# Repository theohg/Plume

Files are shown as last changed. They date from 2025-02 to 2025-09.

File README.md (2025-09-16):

<p align="center" width="100%">
  <picture>
    <source media="(prefers-color-scheme: dark)" srcset="./Logos/Plume_logo_light.png">
    <source media="(prefers-color-scheme: light)" srcset="./Logos/Plume_logo_dark.png">
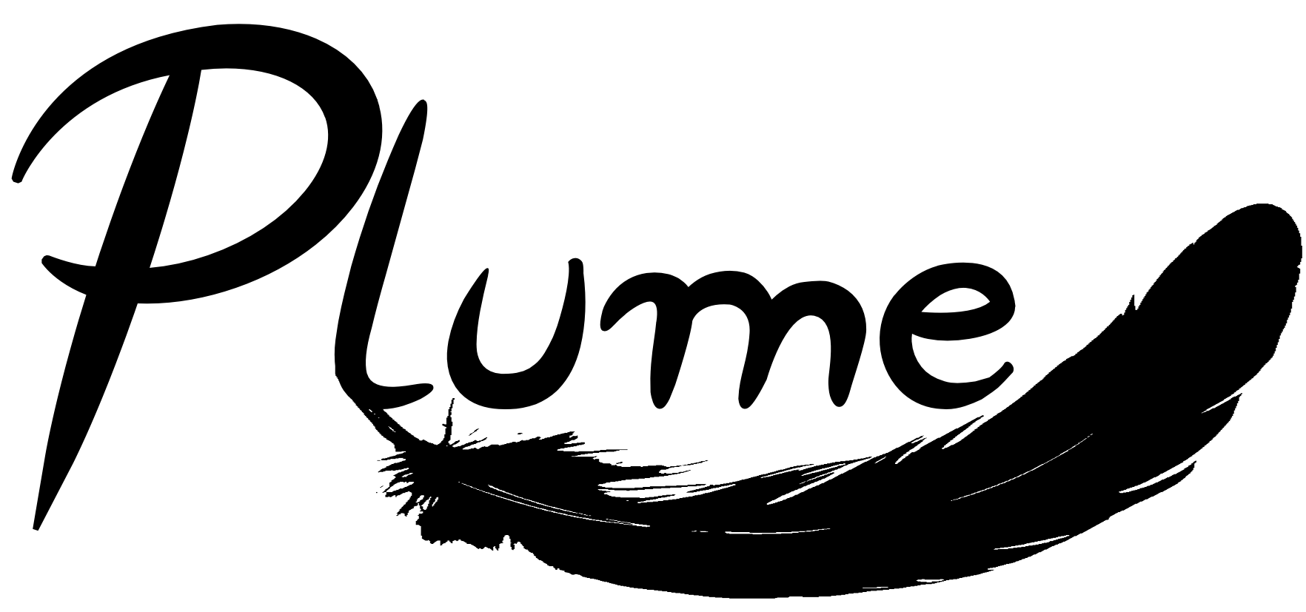
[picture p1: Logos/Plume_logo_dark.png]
Plume logo
    
  </picture>
</p>

Plume was designed by Théo Heng for the Integrated Actuators Laboratory [(LAI)](https://www.epfl.ch/labs/lai/) in the context of a master semester project. The goal is to develop a microcontroller-based system to independently control a motor array in a reconfigurable insole designed for patients with diabetes, redistributing plantar pressure without the use of position sensors. 

This board is capable to drive and control in position up to 18 Brushed DC motors total and up to 9 simultaneously, without position sensors. This is achieved thanks to the ripple counting technique, integrated in the DRV8214 drivers. 

Plume also integrates multiple other features: 
- Automotive Grade Wireless Charging Qi (WPC v2.0) 
- USB-C charging
- Power Path between USB and Induction
- BLE 5.4
- Adressable RGB LED
- Power LED, Charge LED, Fault LEDs
- Exposed UART and I2C interface
- Tag-Connect 2030 for SWD + SWO
- Battery Protection and Voltage Supervisor
- 6-axis, High Performance, low power IMU
- Motion-Controlled Deep-Sleep mode
- I2C Multiplexer
- Accurate and Low-Power Battery Voltage Sensing

***

<p align="center" width="100%">
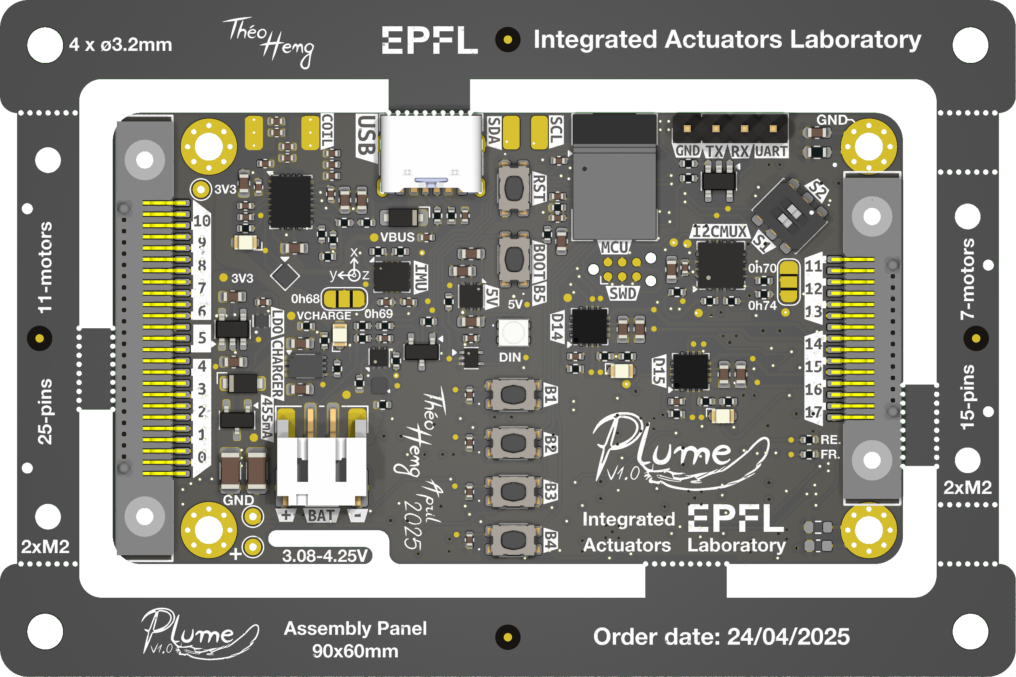
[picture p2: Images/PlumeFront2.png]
    
</p>

<p align="center" width="100%">
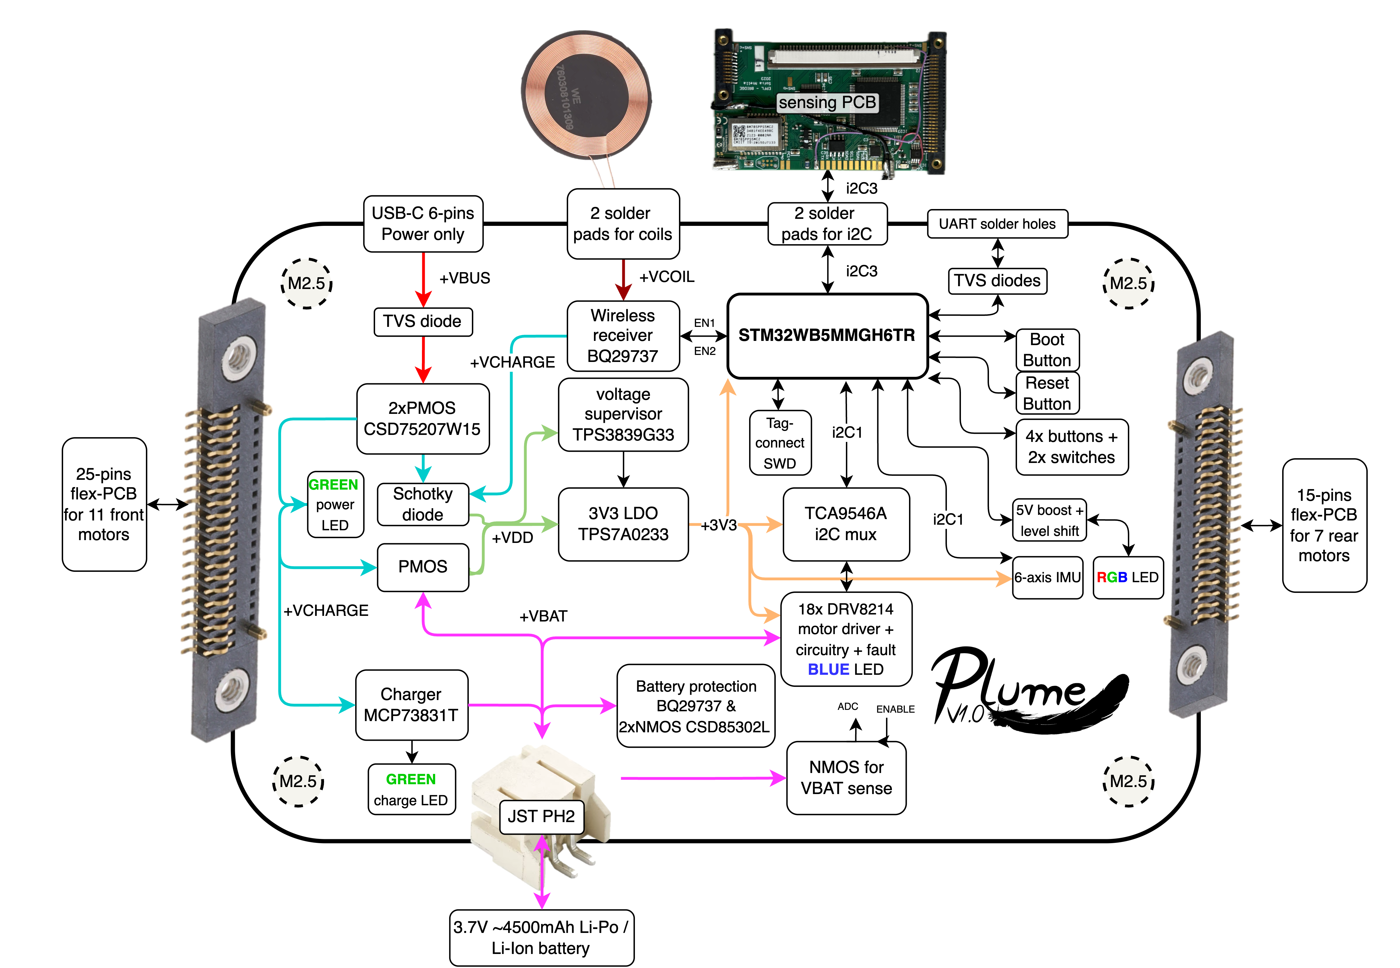
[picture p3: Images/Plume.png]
    
</p>

***

## SPECIFICATIONS

| Parameter | Plume V1.0 | 
| --- | --- |
| Working Battery Voltage Input | 3.08-4.25 V |
| Typ. Charge Current (USB, wireless)| 455 mA |
| Max. Allowed Charge Current | 2.27 A |
| Max. Continuous Discharge Current | 4.54 A |
| Theoretical Deep Sleep Power Consumption| 15 µA |
| Mass | 23.5g with the frame |
| Communication | UART / Trace Asynchronous (SWD) / I2C |
| MCU | STM32 WB5MMGH6TR |
| Dimensions | 70x40x9mm |
| Cost per PCB    | 39 CHF board + 75 CHF components + 125 CHF assembly ≈ 240 CHF / PCB    |
| Designer   | Théo Heng        |
| Supervisors   | Maël Dagon, Paolo Germano      |
| Development Period       | Feb. - May. 2025 |
| Project    | Smart Footwear for Diabetic Foot Care    |

***

## DIRECTORY STRUCTURE

```
Plume
├── Computations        # Computation sheets and simulations performed
├── Datasheets          # Datasheet of components
├── Images              # Pictures and screenshots used in schematics
├── lib
    |── 3d_models       # Component 3D models
    |── lib_fp          # Footprint libraries
    └── lib_sym         # Symbol libraries
├── Logos               # EPFL and Plume logos
├── Manufacturing
    |── Assembly        # BOM, assembly document
        |── bom.csv     # CSV BOM
        |── bom.html    # HTML BOM
        └── ibom        # HTML interactive BOM
    └── Fabrication     # zipped fabrication documents, and other generated documents by JLCToolkit Pluggin
├── Schematic           # PDF of schematic
├── Software            # Firmware of the Board
    |── PLUME_ESP32     # PlatformIO project for the ESP32-based prototype
    └── PLUME_STM32     # STM32CubeIDE project for the Plume PCB
├── STEP_BLENDER_STL    # Step, .pcb3d and stl files of the PCB and its casing
└── Templates           # Title block templates

```

***

## FIRMWARE

<p align="center" width="100%">
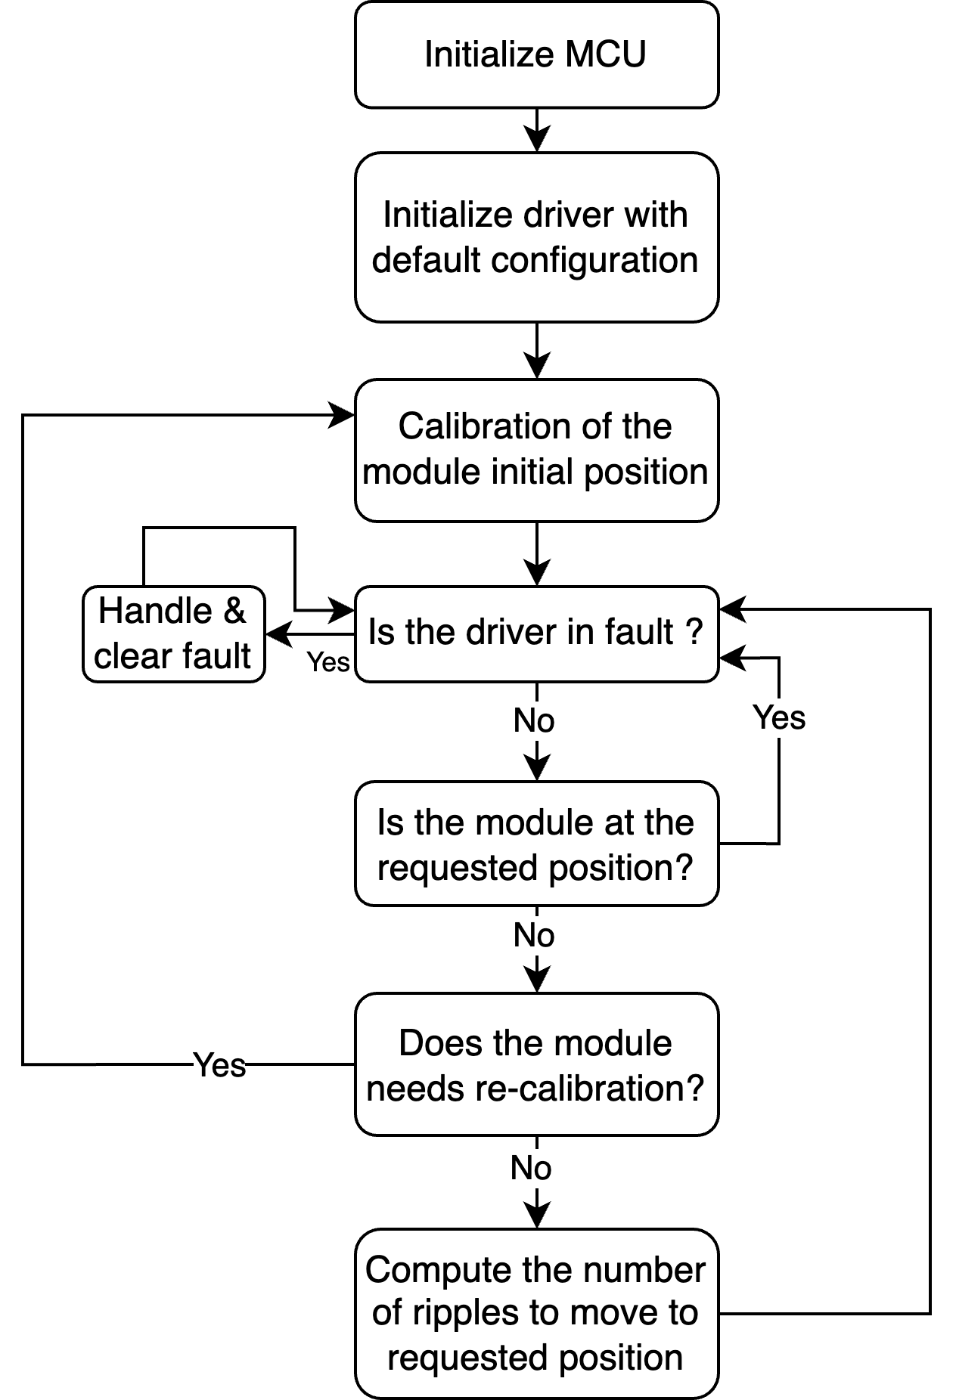
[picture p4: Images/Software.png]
    
</p>

***

## CREDITS

Schematic template & project structure is hugely inspired by the work of Vincent Nguyen on its [Λ M U L E T](https://github.com/EPFLXplore/XRE_LeggedRobot_HW/tree/master/amulet_controller) controler.

***

## PHOTOS

<p align="center" width="100%">
    
</p>

<p align="center" width="100%">
    
</p>

<p align="center" width="100%">
    
</p>

<p align="center" width="100%">
    
</p>

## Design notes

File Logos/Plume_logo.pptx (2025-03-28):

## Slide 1

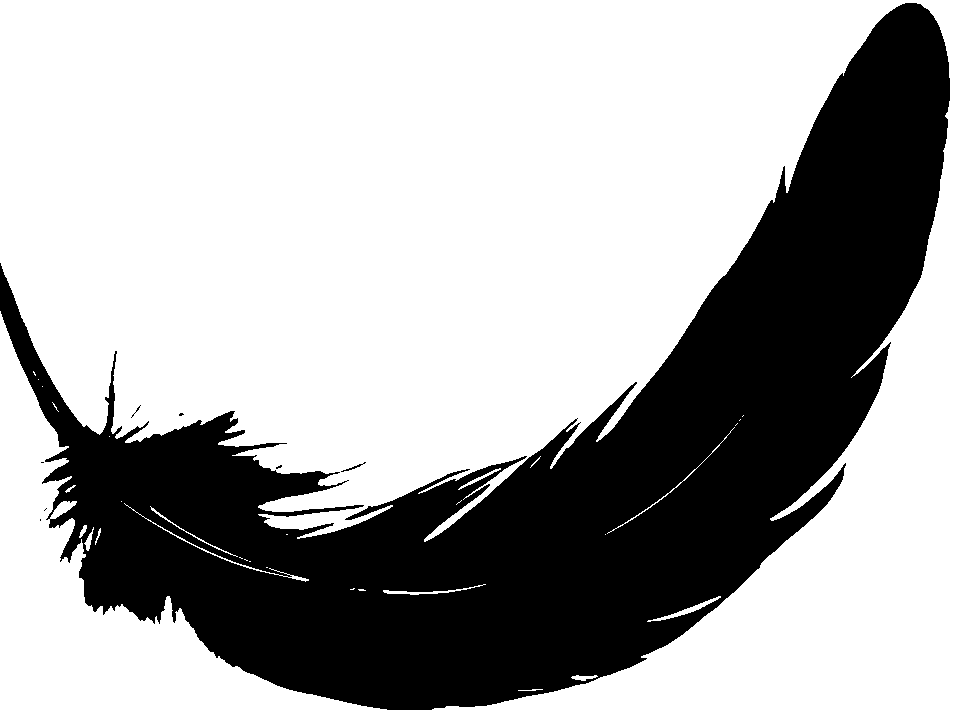
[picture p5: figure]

Plume

V1.0

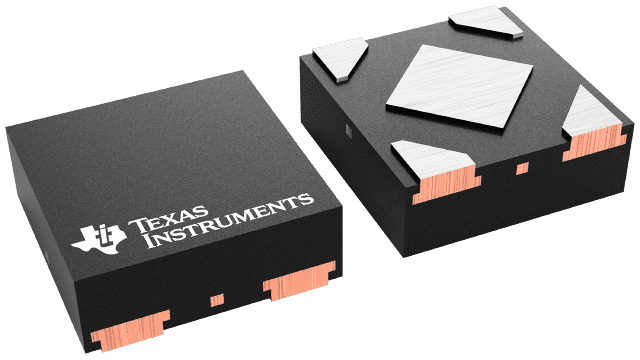
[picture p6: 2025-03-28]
Images/Packages/X2SON_package.png

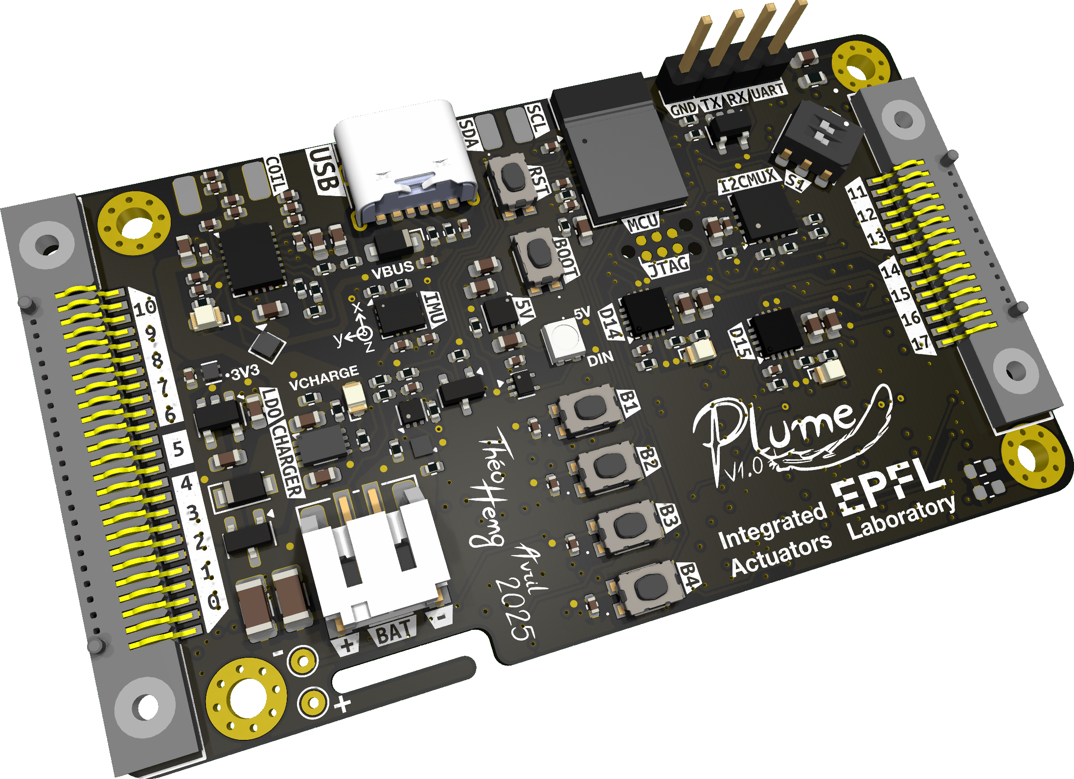
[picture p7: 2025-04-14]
Images/PlumeFront1.png

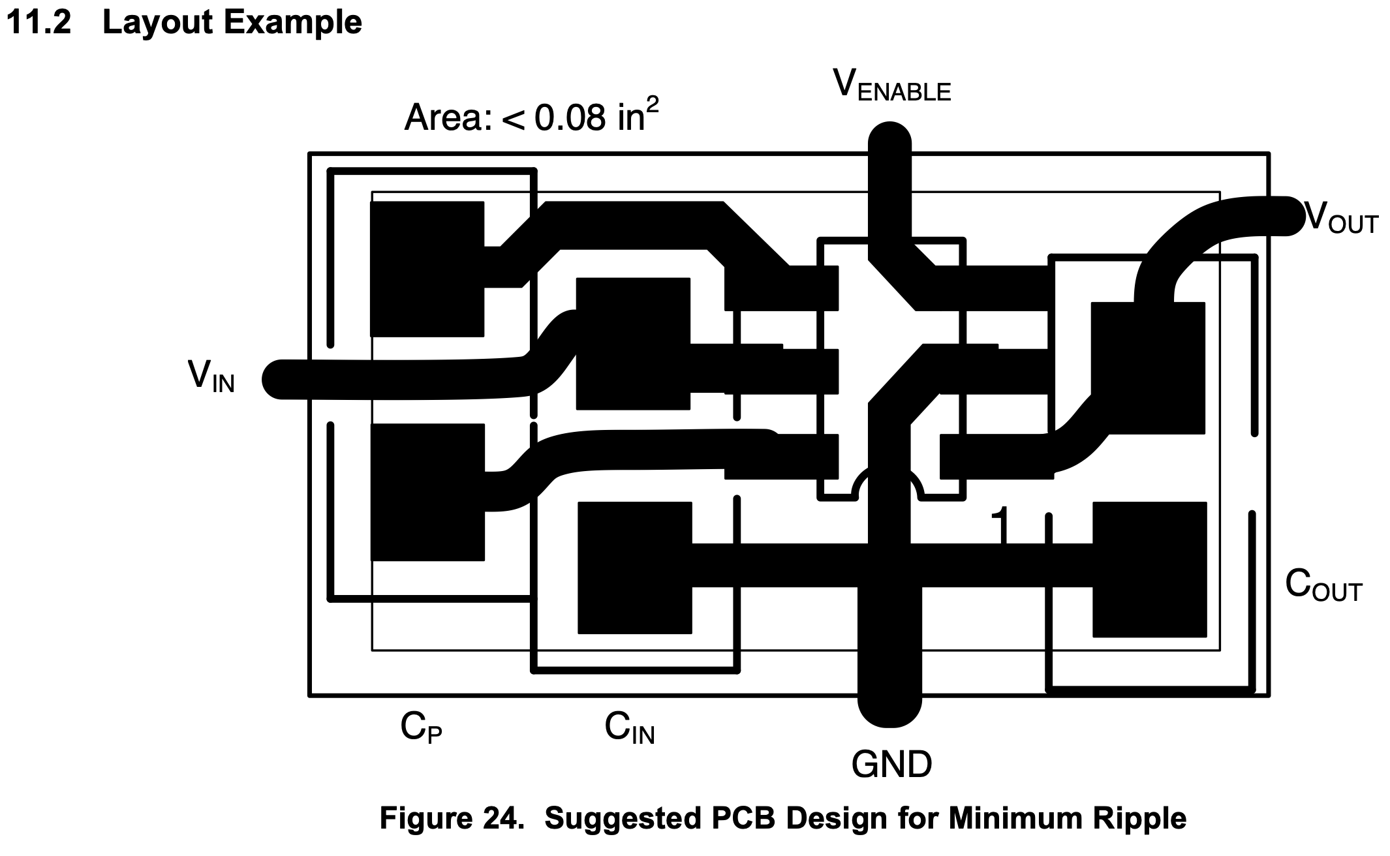
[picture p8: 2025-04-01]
Images/Layouts/Layout_REG71050.png

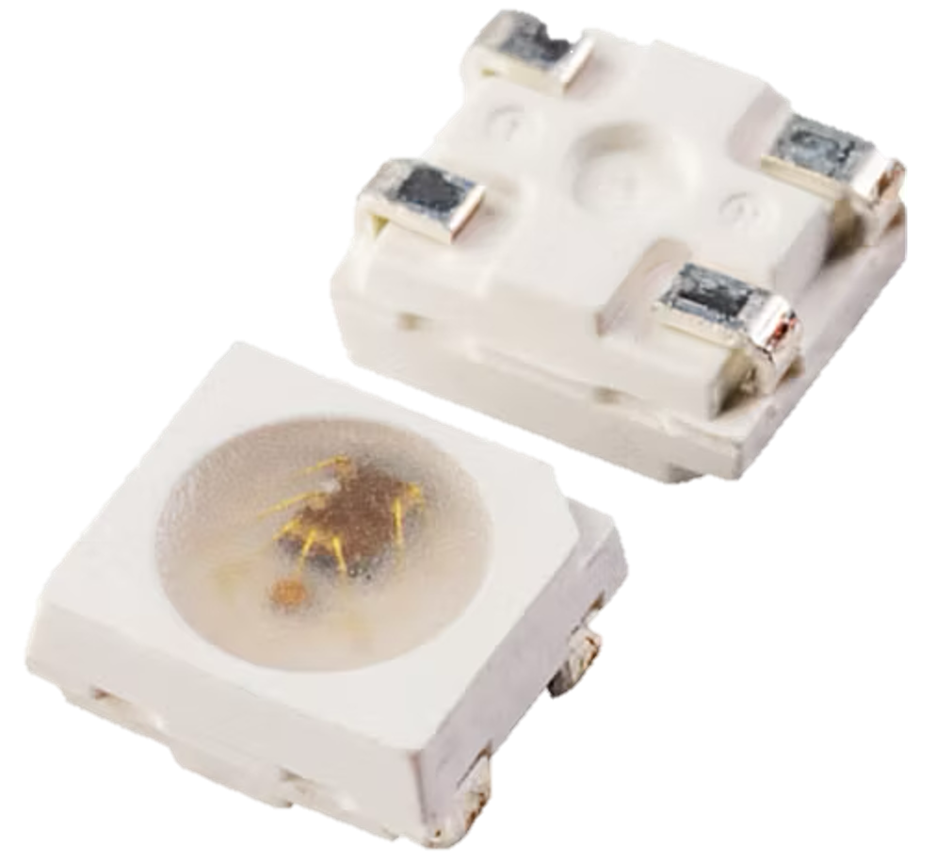
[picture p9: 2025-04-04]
Images/Packages/2427_RGB_LED.png

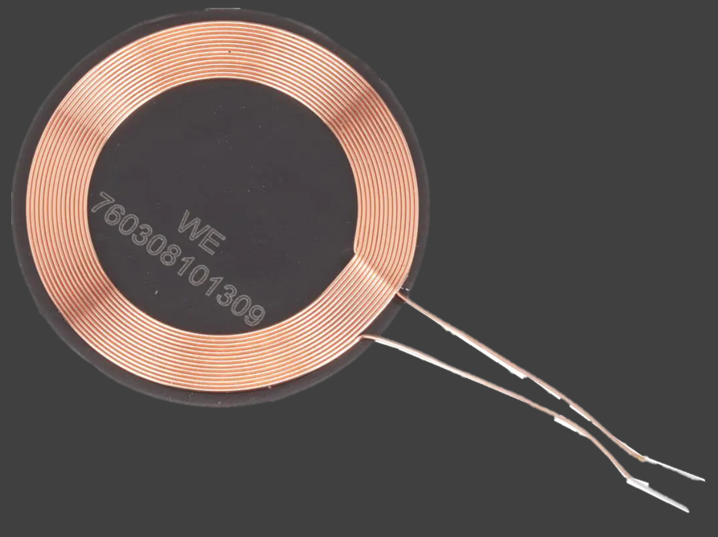
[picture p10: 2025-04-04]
Images/Packages/Coil.png

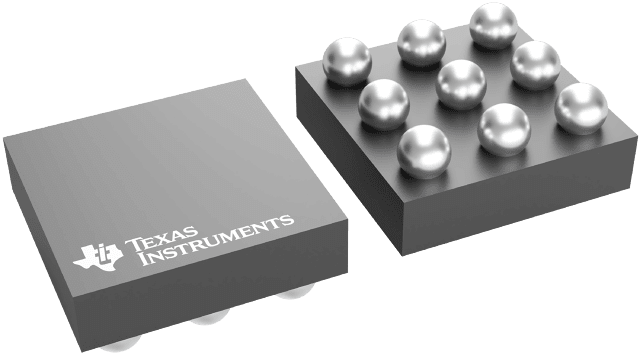
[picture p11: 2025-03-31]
Images/Packages/DSBGA-9_package.png

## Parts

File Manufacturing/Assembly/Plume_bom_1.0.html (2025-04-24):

Source File | Plume.kicad_sch
BoM Date | 2025-04-24T23:43:28+0200
Schematic Version | 1.0
Schematic Date | 2025-04-21
PCB Variant | default
KiCad Version | Eeschema 9.0.0
Component Groups | 53
Component Count (per PCB) | 257
Fitted Components (per PCB) | 251
Number of PCBs | 1
Total Component Count (for 1 PCBs) | 251
 | Description | Part | References | Value | Footprint | Quantity Per PCB | Datasheet | Manufacturer Part Number | Manufacturer | Supplier | Supplier Part Number
1 | Unpolarized capacitor | C_Small | C401 C402 C407 C408 C409 C410 C504 C505 C601 C604 C605 C616 C701 C801 C903 C1001 C1002 C1203 C1303 C1403 C1503 C1603 C1703 C1803 C1903 C2003 C2103 C2203 C2303 C2403 C2503 C2603 C2703 C2803 C2903 | 100n X7R 16V | C_0402_1005Metric | 35 | https://www.mouser.ch/ProductDetail/Samsung-Electro-Mechanics/CL05B104KO5VPNC?qs=SRYZG9HaIQ0dGqjRr5dbew%3D%3D | CL05B104KO5VPNC | Samsung Electro-Mechanics | Mouser Electronics | 187-CL05B104KO5VPNC (https://www.mouser.com/ProductDetail/187-CL05B104KO5VPNC)
2 | Unpolarized capacitor | C_Small | C1202 C1302 C1402 C1502 C1602 C1702 C1802 C1902 C2002 C2102 C2202 C2302 C2402 C2502 C2602 C2702 C2802 C2902 | 100n X7R 50V | C_0603_1608Metric | 18 | https://www.mouser.ch/ProductDetail/KEMET/C0603C104J5RACAUTO?qs=XYJIsZbdjSO3ULwa1DwJaA%3D%3D | C0603C104J5RACAUTO | KEMET | Mouser Electronics | 80-C0603C104J5RAUTO (https://www.mouser.com/ProductDetail/80-C0603C104J5RAUTO)
3 | Unpolarized capacitor | C_Small | C606 C609 C615 | 10n C0G 25V | C_0402_1005Metric | 3 | https://www.mouser.ch/ProductDetail/Murata-Electronics/GRM1555C1E103JE01J?qs=d0WKAl%252BL4Kaf0f%252BHGWOwHQ%3D%3D | GRM1555C1E103JE01J | Murata Electronics | Mouser Electronics | 81-GRM1555C1E103JE1J (https://www.mouser.com/ProductDetail/81-GRM1555C1E103JE1J)
4 | Unpolarized capacitor | C_Small | C602 C617 C618 C702 C703 C1201 C1301 C1401 C1501 C1601 C1701 C1801 C1901 C2001 C2101 C2201 C2301 C2401 C2501 C2601 C2701 C2801 C2901 | 10u X5R 16V | C_0603_1608Metric | 23 | https://www.mouser.ch/ProductDetail/Murata-Electronics/GRM188R61C106MAALD?qs=hNud%2FORuBR3LEOKZ4RJp9w%3D%3D | GRM188R61C106MAALD | Murata Electronics | Mouser Electronics | 81-GRM188R61C106MALD (https://www.mouser.com/ProductDetail/81-GRM188R61C106MALD)
5 | Unpolarized capacitor | C_Small | C610 | 150n X7R 25V | C_0402_1005Metric | 1 | https://www.mouser.ch/ProductDetail/TDK/CGA2B3X7R1E154K050BB?qs=xLDY6iXSiQa5a3ygyaobCg%3D%3D | CGA2B3X7R1E154K050BB | TDK | Mouser Electronics | 810-CGA2B3X7R1E154KB (https://www.mouser.com/ProductDetail/810-CGA2B3X7R1E154KB)
6 | Unpolarized capacitor | C_Small | C3002 | 1n X7R 1kV | C_0603_1608Metric | 1 | https://www.mouser.ch/ProductDetail/KEMET/C0603C102KDRACTU?qs=B0TNOcbsrWfl%252B1TgqaaQlQ%3D%3D | C0603C102KDRACTU | KEMET | Mouser Electronics | 80-C0603C102KDRACTU (https://www.mouser.com/ProductDetail/80-C0603C102KDRACTU)
7 | Unpolarized capacitor | C_Small | C603 C802 | 1u X7R 16V | C_0603_1608Metric | 2 | https://www.mouser.ch/ProductDetail/TDK/CGA3E1X7R1C105K080AC?qs=XHchNesRtUbBVNsGg9%252BP9g%3D%3D | CGA3E1X7R1C105K080AC | TDK | Mouser Electronics | 810-CGA3E1X7R1C105AC (https://www.mouser.com/ProductDetail/810-CGA3E1X7R1C105AC)
8 | Unpolarized capacitor | C_Small | C901 | 220n X7R 16V | C_0603_1608Metric | 1 | https://www.mouser.ch/ProductDetail/TDK/CGA3E2X7R1C224K080AA?qs=NRhsANhppD%252BSF2Ghb8qyBQ%3D%3D | CGA3E2X7R1C224K080AA | TDK | Mouser Electronics | 810-CGA3E2X7R1C224K (https://www.mouser.com/ProductDetail/810-CGA3E2X7R1C224K)
9 | Unpolarized capacitor | C_Small | C608 C614 | 22n X7R 25V | C_0402_1005Metric | 2 | https://www.mouser.ch/ProductDetail/Murata-Electronics/GCM155R71E223KA55D?qs=QDXoN8f0aYJ3xbAG%252B51q9g%3D%3D | GCM155R71E223KA55D | Murata Electronics | Mouser Electronics | 81-GCM155R71E223KA5D (https://www.mouser.com/ProductDetail/81-GCM155R71E223KA5D)
10 | Unpolarized capacitor | C_Small | C611 | 2n2 X7R 25V | C_0402_1005Metric | 1 | https://www.mouser.ch/ProductDetail/TAIYO-YUDEN/TMF105B7222KVHF?qs=%252B6g0mu59x7L2OaVQBnCjqw%3D%3D | TMF105B7222KVHF | TAIYO YUDEN | Mouser Electronics | 963-TMF105B7222KVHF (https://www.mouser.com/ProductDetail/963-TMF105B7222KVHF)
11 | Unpolarized capacitor | C_Small | C902 C904 | 2u2 X7R 16V | C_0603_1608Metric | 2 | https://www.mouser.ch/ProductDetail/Murata-Electronics/GRM188Z71C225KE43D?qs=Ey7%2FXF42M3cR7ECLHyzpoA%3D%3D | GRM188Z71C225KE43D | Murata Electronics | Mouser Electronics | 81-GRM188Z71C225KE3D (https://www.mouser.com/ProductDetail/81-GRM188Z71C225KE3D)
12 | Unpolarized capacitor | C_Small | C612 | 390pF X7R 25V | C_0402_1005Metric | 1 | https://www.mouser.ch/ProductDetail/Vishay-Vitramon/VJ0402Y391JXXCW1BC?qs=f5fGhOx873TBeKjaAqsdYg%3D%3D | VJ0402Y391JXXCW1BC | Vishay / Vitramon | Mouser Electronics | 77-VJ0402Y391JXXCBC (https://www.mouser.com/ProductDetail/77-VJ0402Y391JXXCBC)
13 | Unpolarized capacitor | C_Small | C607 C613 | 470n X5R 25V | C_0402_1005Metric | 2 | https://www.mouser.ch/ProductDetail/Murata-Electronics/GRT155R61E474KE01D?qs=drgMNd%252BkGPMC62u63CQDfw%3D%3D | GRT155R61E474KE01D | Murata Electronics | Mouser Electronics | 81-GRT155R61E474KE1D (https://www.mouser.com/ProductDetail/81-GRT155R61E474KE1D)
14 | Unpolarized capacitor | C_Small | C501 C502 | 47u X5R 16V | C_1206_3216Metric | 2 | https://www.mouser.ch/ProductDetail/TAIYO-YUDEN/MSASE31LBB5476MTNA01?qs=tlsG%2FOw5FFhhPmEmFzorng%3D%3D | MSASE31LBB5476MTNA01 | TAIYO YUDEN | Mouser Electronics | 963-MSASE31LBB5476MT (https://www.mouser.com/ProductDetail/963-MSASE31LBB5476MT)
15 | Unpolarized capacitor | C_Small | C403 C503 C506 | 4u7 X7R 16V | C_0603_1608Metric | 3 | https://www.mouser.ch/ProductDetail/Murata-Electronics/GRM188Z71C475KE21D?qs=d0WKAl%252BL4KajNOvalhHKtQ%3D%3D | GRM188Z71C475KE21D | Murata Electronics | Mouser Electronics | 81-GRM188Z71C475KE1D (https://www.mouser.com/ProductDetail/81-GRM188Z71C475KE1D)
16 | ESD Protection Diodes / TVS Diodes Quad 4.5-pF 3.6-V +/-30-kV ESD protect | ESDS314 | D401 | ESDS314 | SOT-23-5-TEXAS | 1 | https://www.ti.com/lit/ds/symlink/esds314.pdf?ts=1743702062530 | ESDS314DBVR | Texas Instruments | Mouser Electronics | 595-ESDS314DBVR (https://www.mouser.com/ProductDetail/595-ESDS314DBVR)
17 | 2427 RGB LED 4-Pin with Integrated IC | IN-PI22TAT5R5G5B | D901 | IN-PI22TAT5R5G5B | INPI22TAT5R5G5B | 1 | https://www.inolux-corp.com/datasheet/SMDLED/Addressable%20LED/IN-PI22TAT5R5G5B_v1.2.pdf | IN-PI22TAT5R5G5B | Inolux | Mouser Electronics | 743-IN-PI22TAT5R5G5B (https://www.mouser.com/ProductDetail/743-IN-PI22TAT5R5G5B)
18 | Schottky diode | D_Schottky | D701 | Schottky 1N5819W | Nexperia_CFP3_SOD-123W | 1 | https://assets.nexperia.com/documents/data-sheet/PMEG60T20ELR.pdf | PMEG60T20ELRX | Nexperia | Mouser Electronics | 771-PMEG60T20ELRX (https://www.mouser.com/ProductDetail/771-PMEG60T20ELRX)
19 | Zener diode | D_Zener | D601 | TVS SMF5.0A | D_SOD-123FL | 1 | https://www.littelfuse.com/assetdocs/tvs-diodes-smf-datasheet?assetguid=7EB8A5B6-BDD0-4561-8F19-0C3CC6F9B2AF | SMF5.0A | Littelfuse | Mouser Electronics | 576-SMF5.0A (https://www.mouser.com/ProductDetail/576-SMF5.0A)
20 | 2-A Brushed DC Motor Driver with Ripple Counting, Stall Detection, and Speed Regulation | DRV8214RTER | IC1201 IC1301 IC1401 IC1501 IC1601 IC1701 IC1801 IC1901 IC2001 IC2101 IC2201 IC2301 IC2401 IC2501 IC2601 IC2701 IC2801 IC2901 | DRV8214RTER | WQFN-16-1EP_3x3mm_P0.5mm_EP1.68x1.68mm_ThermalVias | 18 | https://www.ti.com/lit/ds/symlink/drv8214.pdf?ts=1743082368801 | DRV8214RTER | Texas Instruments | Mouser Electronics | 595-DRV8214RTER (https://www.mouser.com/ProductDetail/595-DRV8214RTER)
21 | 60-mA, 5.0-V, Buck/Boost Charge Pump in ThinSOT-23 | REG71050DRVT | IC902 | REG71050DRVR | WSON-6-1EP_2x2mm_P0.65mm_EP1x1.6mm | 1 | https://www.ti.com/lit/ds/symlink/reg71050.pdf?ts=1743455923124 | REG71050DRVR | Texas Instruments | Mouser Electronics | 595-REG71050DRVR (https://www.mouser.com/ProductDetail/595-REG71050DRVR)
22 | Single Bus Buffer Gate With 3-State Output | SN74AHCT1G125DRLR | IC901 | SN74AHCT1G125DRLR | SOT-553 | 1 | https://www.ti.com/lit/ds/symlink/sn74ahct1g125.pdf?ts=1743406415648 | SN74AHCT1G125DRLR | Texas Instruments | Mouser Electronics | 595-SN74AHCT1G125DRL (https://www.mouser.com/ProductDetail/595-SN74AHCT1G125DRL)
23 | CONN HEADER SMD R/A 2POS 2MM | CONN_S2B-PH-SM4-TB_JST | J502 | S2B-PH-SM4-TB | CONN_S2B-PH-SM4-TB_JST | 1 | https://www.jst-mfg.com/product/pdf/eng/ePH.pdf | S2B-PH-SM4-TB(LF)(SN) | JST Commercial | Mouser Electronics | 306-S2BPHSM4TBLFSN (https://www.mouser.com/ProductDetail/306-S2BPHSM4TBLFSN)
24 | USB Power-Only 6P Type-C Receptacle connector | USB_C_Receptacle_PowerOnly_6P | J602 | USB_C_Receptacle_PowerOnly_6P | USB4125-GF-A | 1 | https://www.mouser.ch/datasheet/2/837/GCT_USB4125_Product_Drawing-3538561.pdf | USB4125-GF-A | GCT | Mouser Electronics | 640-USB4125-GF-A (https://www.mouser.com/ProductDetail/640-USB4125-GF-A)
25 | Single Colour LEDs 0603 Dome Lens LED Blue- 465nm | LED | LED1201 LED1301 LED1401 LED1501 LED1601 LED1701 LED1801 LED1901 LED2001 LED2101 LED2201 LED2301 LED2401 LED2501 LED2601 LED2701 LED2801 LED2901 | BLUE | LED_0603_KingBright | 18 | https://www.mouser.ch/datasheet/2/216/APTD1608LQBC_D-1102154.pdf | APTD1608LQBC/D | Kingbright | Mouser Electronics | 604-APTD1608LQBCD (https://www.mouser.com/ProductDetail/604-APTD1608LQBCD)
26 | Light emitting diode | LED | LED501 LED601 | GREEN | LED_0603_KingBright | 2 | https://www.mouser.ch/datasheet/2/216/APT1608CGCK-24002.pdf | APT1608CGCK | Kingbright | Mouser Electronics | 604-APT1608CGCK (https://www.mouser.com/ProductDetail/604-APT1608CGCK)
27 | MOSFET Dual P-CH NexFET Pwr MOSFET | CSD75207W15 | Q601 | CSD75207W15 | Texas_DSBGA-9_1.62x1.58mm_Layout3x3_P0.5mm | 1 | https://www.ti.com/lit/ds/symlink/csd75207w15.pdf?ts=1743083254353 | CSD75207W15 | Texas Instruments | Mouser Electronics | 595-CSD75207W15 (https://www.mouser.com/ProductDetail/595-CSD75207W15)
28 | 20V, N ch NexFET MOSFET, dual common drain LGA 1.35x1.35, 24mOhm | CSD85302L | Q502 | CSD85302L | CSD85302L | 1 | http://www.ti.com/lit/ds/symlink/csd85302l.pdf | CSD85302L | Texas Instruments | Mouser Electronics | 595-CSD85302L (https://www.mouser.com/ProductDetail/595-CSD85302L)
29 | MOSFETs MOSFT 5.0A 29mOhm 30V 2.5V drv capable | Q_NMOS_Depletion_GSD | Q501 | NMOS IRLML6344TRPBF SOT-23 | SOT-23 | 1 | https://www.mouser.ch/datasheet/2/196/Infineon_IRLML6344_DataSheet_v01_01_EN-3363406.pdf | IRLML6344TRPBF | Infineon Technologies | Mouser Electronics | 942-IRLML6344TRPBF (https://www.mouser.com/ProductDetail/942-IRLML6344TRPBF)
30 | P-MOSFET transistor, gate/source/drain | Q_PMOS_GSD | Q701 | PMOS SI2365EDS-T1-GE3 | SOT-23-3 | 1 | https://www.vishay.com/docs/63199/si2365eds.pdf | SI2365EDS-T1-GE3 | Vishay Semiconductors | Mouser Electronics | 78-SI2365EDS-T1-GE3 (https://www.mouser.com/ProductDetail/78-SI2365EDS-T1-GE3)
31 | Resistor, small symbol | R_Small | R3002 | 0R 1% | R_0603_1608Metric | 1 | https://www.mouser.ch/ProductDetail/YAGEO/RC0603FR-100RL?qs=gY0y7AQI9SNjcfwXbqIKbg%3D%3D | RC0603FR-100RL | YAGEO | Mouser Electronics | 603-RC0603FR-100RL (https://www.mouser.com/ProductDetail/603-RC0603FR-100RL)
32 | Resistor | R_Small | R404 R406 R509 R701 R801 R901 R1203 R1303 R1403 R1503 R1603 R1703 R1803 R1903 R2003 R2103 R2203 R2303 R2403 R2503 R2603 R2703 R2803 R2903 | 100k 1% | R_0402_1005Metric | 24 | https://www.mouser.ch/ProductDetail/Panasonic/ERJ-2RKF1003X?qs=H7k1u0Mp9JQnXoBKdf15Qg%3D%3D | ERJ-2RKF1003X | Panasonic | Mouser Electronics | 667-ERJ-2RKF1003X (https://www.mouser.com/ProductDetail/667-ERJ-2RKF1003X)
33 | Resistor | R_Small | R402 R503 R605 R606 R608 | 10k 1% | R_0402_1005Metric | 5 | https://www.mouser.ch/ProductDetail/KOA-Speer/RK73H1ETTPB1002F?qs=sGAEpiMZZMvdGkrng054t65cMycmke1dK22GtXiM9hM%3D | RK73H1ETTPB1002F | KOA Speer | Mouser Electronics | 660-RK73H1ETTPB1002F (https://www.mouser.com/ProductDetail/660-RK73H1ETTPB1002F)
34 | Resistor | R_Small | R604 R607 | 196R 1% | R_0402_1005Metric | 2 | https://www.mouser.ch/ProductDetail/Vishay-Dale/CRCW0402196RFKED?qs=9Aka%2FNDvCXC%2FtFusjSrxBQ%3D%3D | CRCW0402196RFKED | Vishay / Dale | Mouser Electronics | 71-CRCW0402196RFKED (https://www.mouser.com/ProductDetail/71-CRCW0402196RFKED)
35 | Resistor | R_Small | R403 R405 | 22R 1% | R_0402_1005Metric | 2 | https://www.mouser.ch/ProductDetail/KOA-Speer/RK73H1ETTP22R0F | RK73H1ETTP22R0F | KOA Speer | Mouser Electronics | 660-RK73H1ETTP22R0F (https://www.mouser.com/ProductDetail/660-RK73H1ETTP22R0F)
36 | Resistor | R_Small | R504 R508 | 2k2 1% | R_0402_1005Metric | 2 | https://www.mouser.ch/ProductDetail/KOA-Speer/RK73H1ETTP2201F?qs=oI046glRuruobG9rEu19Sw%3D%3D | RK73H1ETTP2201F | KOA Speer | Mouser Electronics | 660-RK73H1ETTP2201F (https://www.mouser.com/ProductDetail/660-RK73H1ETTP2201F)
37 | Resistor | R_Small | R401 R501 R505 R601 R1202 R1302 R1402 R1502 R1602 R1702 R1802 R1902 R2002 R2102 R2202 R2302 R2402 R2502 R2602 R2702 R2802 R2902 | 330R 1% | R_0402_1005Metric | 22 | https://www.mouser.ch/ProductDetail/KOA-Speer/RK73H1ETTP3300F?qs=4CJzfoelV6C3hCuuGB%2F5LQ%3D%3D | RK73H1ETTP3300F | KOA Speer | Mouser Electronics | 660-RK73H1ETTP3300F (https://www.mouser.com/ProductDetail/660-RK73H1ETTP3300F)
38 | Resistor | R_Small | R502 R802 R803 R804 R805 R806 R807 R1001 R1002 | 3k 1% | R_0402_1005Metric | 9 | https://www.mouser.ch/ProductDetail/KOA-Speer/RK73H1ETTP3001F?qs=pim%252BJ6MgNfS80Tm8%2FkBkXQ%3D%3D | RK73H1ETTP3001F | KOA Speer | Mouser Electronics | 660-RK73H1ETTP3001F (https://www.mouser.com/ProductDetail/660-RK73H1ETTP3001F)
39 | Resistor | R_Small | R506 R507 | 4M99 1% | R_0402_1005Metric | 2 | https://www.mouser.ch/ProductDetail/KOA-Speer/RK73H1ETTP4994F?qs=v3ImdA%2FOTSQZBfUeBz4Q8A%3D%3D | RK73H1ETTP4994F | KOA Speer | Mouser Electronics | 660-RK73H1ETTP4994F (https://www.mouser.com/ProductDetail/660-RK73H1ETTP4994F)
40 | Resistor | R | R602 R603 | 5k1 1% | R_0402_1005Metric | 2 | https://www.mouser.ch/ProductDetail/KOA-Speer/RK73H1ETTP5101F?qs=0Mn4dg0AsPAhhJD1ZsgV0Q%3D%3D | RK73H1ETTP5101F | KOA Speer | Mouser Electronics | 660-RK73H1ETTP5101F (https://www.mouser.com/ProductDetail/660-RK73H1ETTP5101F)
41 | Resistor | R_Small | R1201 R1301 R1401 R1501 R1601 R1701 R1801 R1901 R2001 R2101 R2201 R2301 R2401 R2501 R2601 R2701 R2801 R2901 | 680R 1% | R_0402_1005Metric | 18 | https://www.mouser.fr/ProductDetail/Vishay-Dale/CRCW0402680RFKEDC?qs=E3Y5ESvWgWPmgUvh1o91RA%3D%3D | CRCW0402680RFKEDC | Vishay / Dale | Mouser Electronics | 71-CRCW0402680RFKEDC (https://www.mouser.com/ProductDetail/71-CRCW0402680RFKEDC)
42 | Slide Switches Dual SPDT, ON-ON, slide, J-hook SMD terminals, 100mA @ 6V DC, T&R packaging, non-washable without seal tape | CAS-D20A1 | SW403 | CAS-D20A1 | CAS-D2xx | 1 | https://www.mouser.ch/datasheet/2/972/cas-1628136.pdf | CAS-D20TA1 | Nidec Components | Mouser Electronics | 229-CAS-D20TA1 (https://www.mouser.com/ProductDetail/229-CAS-D20TA1)
43 | Tactile Switches SMT Micro Miniature Tactile Switch with 1.9 mm Height Actuator | KMR2_series | SW401 SW402 SW404 SW405 SW406 SW407 | KMR232NG ULC | SW_KMR232NGULCLFS | 6 | https://www.ckswitches.com/media/1479/kmr2.pdf | KMR232NG ULC LFS | C&K | Mouser Electronics | 611-KMR232NGULCLFS (https://www.mouser.com/ProductDetail/611-KMR232NGULCLFS)
44 | 6-axis, low-power, smart IMU | BMI270 | U1001 | BMI270 | Bosch_LGA-14_3x2.5mm_P0.5mm | 1 | https://www.bosch-sensortec.com/media/boschsensortec/downloads/datasheets/bst-bmi270-ds000.pdf | BMI270 | Bosch Sensortec | Mouser Electronics | 262-BMI270 (https://www.mouser.com/ProductDetail/262-BMI270)
45 | Voltage and Current Protection for Single-Cell Li-Ion and Li-Polymer Batteries | BQ297xy | U501 | BQ29737DSER | WSON-6_1.5x1.5mm_P0.5mm | 1 | http://www.ti.com/lit/ds/symlink/bq2970.pdf | BQ29737DSER | Texas Instruments | Mouser Electronics | 595-BQ29737DSER (https://www.mouser.com/ProductDetail/595-BQ29737DSER)
46 | Automotive Highly Integrated Wireless Receiver Qi (WPC v2.0) Compliant Power Supply | BQ51013CQWRHLRQ1 | U601 | BQ51013CQWRHLRQ1 | Texas_VQFN-RHL-20 | 1 | https://www.ti.com/lit/ds/symlink/bq51013c-q1.pdf?ts=1743760265944 | BQ51013CQWRHLRQ1 | Texas Instruments | Mouser Electronics | 595-BQ51013CQWRHLRQ1 (https://www.mouser.com/ProductDetail/595-BQ51013CQWRHLRQ1)
47 | Miniature Single-Cell, Fully Integrated Li-Ion, Li-Polymer Charge Management Controllers | MCP73831T-2ACI/MC | U502 | MCP73831T-2ACI/MC | DFN_2x3mm | 1 | https://www.mouser.ch/datasheet/2/268/MCP73831_Family_Data_Sheet_DS20001984H-3441711.pdf | MCP73831T-2ACI/MC | Microchip Technology | Mouser Electronics | 579-MCP73831T-2ACIMC (https://www.mouser.com/ProductDetail/579-MCP73831T-2ACIMC)
48 | Low Voltage 4-Channel I2C and SMBus Switch with Reset Function | PCA9546ARGVR | U801 | PCA9546ARGVR | Texas_RSA_VQFN-16-1EP_4x4mm_P0.65mm_EP2.16x2.16mm | 1 | https://www.ti.com/lit/ds/symlink/pca9546a.pdf?ts=1743761042172 | PCA9546ARGVR | Texas Instruments | Mouser Electronics | 595-PCA9546ARGVR (https://www.mouser.com/ProductDetail/595-PCA9546ARGVR)
49 | ST Microelectronics STM32WB55VG ARM Cortex Bluetooth Low Energy 5.0, Zigbee and 802.15.4 module, 1 MB Flash, 256kb RAM, Fully integrated BOM | STM32WB5MMG | U401 | STM32WB5MMGH6TR | ST-SiP-LGA-86-11x7.3mm | 1 | https://www.st.com/resource/en/datasheet/stm32wb5mmg.pdf | STM32WB5MMGH6TR | STMicroelectronics | Mouser Electronics | 511-STM32WB5MMGH6TR (https://www.mouser.com/ProductDetail/511-STM32WB5MMGH6TR)
50 | 150-nA, Ultralow Power, Supply Voltage Monitor, X2SON-4 | TPS3839DQN | U701 | TPS3839G33DQNR | Texas_X2SON-4_1x1mm_P0.65mm | 1 | http://www.ti.com/lit/ds/sbvs193d/sbvs193d.pdf | TPS3839G33DQNR | Texas Instruments | Mouser Electronics | 595-TPS3839G33DQNR (https://www.mouser.com/ProductDetail/595-TPS3839G33DQNR)
51 | TPS7A02 Nanopower IQ, 25-nA, 200-mA, Low-Dropout Voltage Regulator With Fast Transient Response | TPS7A02xxxDBVR | U702 | TPS7A0233DBVR | SOT-23-5-TEXAS | 1 | https://www.ti.com/lit/ds/symlink/tps7a02.pdf?ts=1745064259825 | TPS7A0233DBVR | Texas Instruments | Mouser Electronics | 595-TPS7A0233DBVR (https://www.mouser.com/ProductDetail/595-TPS7A0233DBVR)
 | Description | Part | References | Value | Footprint | Quantity Per PCB | Datasheet | Manufacturer Part Number | Manufacturer | Supplier | Supplier Part Number
1 | Unpolarized capacitor | C_Small | C3001 C3003 C3004 | 1n X7R 1kV | C_0603_1608Metric | 3 (DNF) | https://www.mouser.ch/ProductDetail/KEMET/C0603C102KDRACTU?qs=B0TNOcbsrWfl%252B1TgqaaQlQ%3D%3D | C0603C102KDRACTU | KEMET | Mouser Electronics | 80-C0603C102KDRACTU (https://www.mouser.com/ProductDetail/80-C0603C102KDRACTU)
2 | Resistor, small symbol | R_Small | R3001 R3003 R3004 | 0R 1% | R_0603_1608Metric | 3 (DNF) | https://www.mouser.ch/ProductDetail/YAGEO/RC0603FR-100RL?qs=gY0y7AQI9SNjcfwXbqIKbg%3D%3D | RC0603FR-100RL | YAGEO | Mouser Electronics | 603-RC0603FR-100RL (https://www.mouser.com/ProductDetail/603-RC0603FR-100RL)

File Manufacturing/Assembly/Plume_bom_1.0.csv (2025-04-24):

Component | Description | Part | References | Value | Footprint | Quantity Per PCB | Datasheet | Manufacturer Part Number | Supplier | Manufacturer | Supplier Part Number
1 | Unpolarized capacitor | C_Small | C401 C402 C407 C408 C409 C410 C504 C505 C601 C604 C605 C616 C701 C801 C903 C1001 C1002 C1203 C1303 C1403 C1503 C1603 C1703 C1803 C1903 C2003 C2103 C2203 C2303 C2403 C2503 C2603 C2703 C2803 C2903 | 100n X7R 16V | C_0402_1005Metric | 35 | https://www.mouser.ch/ProductDetail/Samsung-Electro-Mechanics/CL05B104KO5VPNC?qs=SRYZG9HaIQ0dGqjRr5dbew%3D%3D | CL05B104KO5VPNC | Mouser Electronics | Samsung Electro-Mechanics | 187-CL05B104KO5VPNC
2 | Unpolarized capacitor | C_Small | C1202 C1302 C1402 C1502 C1602 C1702 C1802 C1902 C2002 C2102 C2202 C2302 C2402 C2502 C2602 C2702 C2802 C2902 | 100n X7R 50V | C_0603_1608Metric | 18 | https://www.mouser.ch/ProductDetail/KEMET/C0603C104J5RACAUTO?qs=XYJIsZbdjSO3ULwa1DwJaA%3D%3D | C0603C104J5RACAUTO | Mouser Electronics | KEMET | 80-C0603C104J5RAUTO
3 | Unpolarized capacitor | C_Small | C606 C609 C615 | 10n C0G 25V | C_0402_1005Metric | 3 | https://www.mouser.ch/ProductDetail/Murata-Electronics/GRM1555C1E103JE01J?qs=d0WKAl%252BL4Kaf0f%252BHGWOwHQ%3D%3D | GRM1555C1E103JE01J | Mouser Electronics | Murata Electronics | 81-GRM1555C1E103JE1J
4 | Unpolarized capacitor | C_Small | C602 C617 C618 C702 C703 C1201 C1301 C1401 C1501 C1601 C1701 C1801 C1901 C2001 C2101 C2201 C2301 C2401 C2501 C2601 C2701 C2801 C2901 | 10u X5R 16V | C_0603_1608Metric | 23 | https://www.mouser.ch/ProductDetail/Murata-Electronics/GRM188R61C106MAALD?qs=hNud%2FORuBR3LEOKZ4RJp9w%3D%3D | GRM188R61C106MAALD | Mouser Electronics | Murata Electronics | 81-GRM188R61C106MALD
5 | Unpolarized capacitor | C_Small | C610 | 150n X7R 25V | C_0402_1005Metric | 1 | https://www.mouser.ch/ProductDetail/TDK/CGA2B3X7R1E154K050BB?qs=xLDY6iXSiQa5a3ygyaobCg%3D%3D | CGA2B3X7R1E154K050BB | Mouser Electronics | TDK | 810-CGA2B3X7R1E154KB
6 | Unpolarized capacitor | C_Small | C3002 | 1n X7R 1kV | C_0603_1608Metric | 1 | https://www.mouser.ch/ProductDetail/KEMET/C0603C102KDRACTU?qs=B0TNOcbsrWfl%252B1TgqaaQlQ%3D%3D | C0603C102KDRACTU | Mouser Electronics | KEMET | 80-C0603C102KDRACTU
7 | Unpolarized capacitor | C_Small | C603 C802 | 1u X7R 16V | C_0603_1608Metric | 2 | https://www.mouser.ch/ProductDetail/TDK/CGA3E1X7R1C105K080AC?qs=XHchNesRtUbBVNsGg9%252BP9g%3D%3D | CGA3E1X7R1C105K080AC | Mouser Electronics | TDK | 810-CGA3E1X7R1C105AC
8 | Unpolarized capacitor | C_Small | C901 | 220n X7R 16V | C_0603_1608Metric | 1 | https://www.mouser.ch/ProductDetail/TDK/CGA3E2X7R1C224K080AA?qs=NRhsANhppD%252BSF2Ghb8qyBQ%3D%3D | CGA3E2X7R1C224K080AA | Mouser Electronics | TDK | 810-CGA3E2X7R1C224K
9 | Unpolarized capacitor | C_Small | C608 C614 | 22n X7R 25V | C_0402_1005Metric | 2 | https://www.mouser.ch/ProductDetail/Murata-Electronics/GCM155R71E223KA55D?qs=QDXoN8f0aYJ3xbAG%252B51q9g%3D%3D | GCM155R71E223KA55D | Mouser Electronics | Murata Electronics | 81-GCM155R71E223KA5D
10 | Unpolarized capacitor | C_Small | C611 | 2n2 X7R 25V | C_0402_1005Metric | 1 | https://www.mouser.ch/ProductDetail/TAIYO-YUDEN/TMF105B7222KVHF?qs=%252B6g0mu59x7L2OaVQBnCjqw%3D%3D | TMF105B7222KVHF | Mouser Electronics | TAIYO YUDEN | 963-TMF105B7222KVHF
11 | Unpolarized capacitor | C_Small | C902 C904 | 2u2 X7R 16V | C_0603_1608Metric | 2 | https://www.mouser.ch/ProductDetail/Murata-Electronics/GRM188Z71C225KE43D?qs=Ey7%2FXF42M3cR7ECLHyzpoA%3D%3D | GRM188Z71C225KE43D | Mouser Electronics | Murata Electronics | 81-GRM188Z71C225KE3D
12 | Unpolarized capacitor | C_Small | C612 | 390pF X7R 25V | C_0402_1005Metric | 1 | https://www.mouser.ch/ProductDetail/Vishay-Vitramon/VJ0402Y391JXXCW1BC?qs=f5fGhOx873TBeKjaAqsdYg%3D%3D | VJ0402Y391JXXCW1BC | Mouser Electronics | Vishay / Vitramon | 77-VJ0402Y391JXXCBC
13 | Unpolarized capacitor | C_Small | C607 C613 | 470n X5R 25V | C_0402_1005Metric | 2 | https://www.mouser.ch/ProductDetail/Murata-Electronics/GRT155R61E474KE01D?qs=drgMNd%252BkGPMC62u63CQDfw%3D%3D | GRT155R61E474KE01D | Mouser Electronics | Murata Electronics | 81-GRT155R61E474KE1D
14 | Unpolarized capacitor | C_Small | C501 C502 | 47u X5R 16V | C_1206_3216Metric | 2 | https://www.mouser.ch/ProductDetail/TAIYO-YUDEN/MSASE31LBB5476MTNA01?qs=tlsG%2FOw5FFhhPmEmFzorng%3D%3D | MSASE31LBB5476MTNA01 | Mouser Electronics | TAIYO YUDEN | 963-MSASE31LBB5476MT
15 | Unpolarized capacitor | C_Small | C403 C503 C506 | 4u7 X7R 16V | C_0603_1608Metric | 3 | https://www.mouser.ch/ProductDetail/Murata-Electronics/GRM188Z71C475KE21D?qs=d0WKAl%252BL4KajNOvalhHKtQ%3D%3D | GRM188Z71C475KE21D | Mouser Electronics | Murata Electronics | 81-GRM188Z71C475KE1D
16 | ESD Protection Diodes / TVS Diodes Quad 4.5-pF 3.6-V +/-30-kV ESD protect | ESDS314 | D401 | ESDS314 | SOT-23-5-TEXAS | 1 | https://www.ti.com/lit/ds/symlink/esds314.pdf?ts=1743702062530 | ESDS314DBVR | Mouser Electronics | Texas Instruments | 595-ESDS314DBVR
17 | 2427 RGB LED 4-Pin with Integrated IC | IN-PI22TAT5R5G5B | D901 | IN-PI22TAT5R5G5B | INPI22TAT5R5G5B | 1 | https://www.inolux-corp.com/datasheet/SMDLED/Addressable%20LED/IN-PI22TAT5R5G5B_v1.2.pdf | IN-PI22TAT5R5G5B | Mouser Electronics | Inolux | 743-IN-PI22TAT5R5G5B
18 | Schottky diode | D_Schottky | D701 | Schottky 1N5819W | Nexperia_CFP3_SOD-123W | 1 | https://assets.nexperia.com/documents/data-sheet/PMEG60T20ELR.pdf | PMEG60T20ELRX | Mouser Electronics | Nexperia | 771-PMEG60T20ELRX
19 | Zener diode | D_Zener | D601 | TVS SMF5.0A | D_SOD-123FL | 1 | https://www.littelfuse.com/assetdocs/tvs-diodes-smf-datasheet?assetguid=7EB8A5B6-BDD0-4561-8F19-0C3CC6F9B2AF | SMF5.0A | Mouser Electronics | Littelfuse | 576-SMF5.0A
20 | 2-A Brushed DC Motor Driver with Ripple Counting, Stall Detection, and Speed Regulation | DRV8214RTER | IC1201 IC1301 IC1401 IC1501 IC1601 IC1701 IC1801 IC1901 IC2001 IC2101 IC2201 IC2301 IC2401 IC2501 IC2601 IC2701 IC2801 IC2901 | DRV8214RTER | WQFN-16-1EP_3x3mm_P0.5mm_EP1.68x1.68mm_ThermalVias | 18 | https://www.ti.com/lit/ds/symlink/drv8214.pdf?ts=1743082368801 | DRV8214RTER | Mouser Electronics | Texas Instruments | 595-DRV8214RTER
21 | 60-mA, 5.0-V, Buck/Boost Charge Pump in ThinSOT-23 | REG71050DRVT | IC902 | REG71050DRVR | WSON-6-1EP_2x2mm_P0.65mm_EP1x1.6mm | 1 | https://www.ti.com/lit/ds/symlink/reg71050.pdf?ts=1743455923124 | REG71050DRVR | Mouser Electronics | Texas Instruments | 595-REG71050DRVR
22 | Single Bus Buffer Gate With 3-State Output | SN74AHCT1G125DRLR | IC901 | SN74AHCT1G125DRLR | SOT-553 | 1 | https://www.ti.com/lit/ds/symlink/sn74ahct1g125.pdf?ts=1743406415648 | SN74AHCT1G125DRLR | Mouser Electronics | Texas Instruments | 595-SN74AHCT1G125DRL
23 | CONN HEADER SMD R/A 2POS 2MM | CONN_S2B-PH-SM4-TB_JST | J502 | S2B-PH-SM4-TB | CONN_S2B-PH-SM4-TB_JST | 1 | https://www.jst-mfg.com/product/pdf/eng/ePH.pdf | S2B-PH-SM4-TB(LF)(SN) | Mouser Electronics | JST Commercial | 306-S2BPHSM4TBLFSN
24 | USB Power-Only 6P Type-C Receptacle connector | USB_C_Receptacle_PowerOnly_6P | J602 | USB_C_Receptacle_PowerOnly_6P | USB4125-GF-A | 1 | https://www.mouser.ch/datasheet/2/837/GCT_USB4125_Product_Drawing-3538561.pdf | USB4125-GF-A | Mouser Electronics | GCT | 640-USB4125-GF-A
25 | Single Colour LEDs 0603 Dome Lens LED Blue- 465nm | LED | LED1201 LED1301 LED1401 LED1501 LED1601 LED1701 LED1801 LED1901 LED2001 LED2101 LED2201 LED2301 LED2401 LED2501 LED2601 LED2701 LED2801 LED2901 | BLUE | LED_0603_KingBright | 18 | https://www.mouser.ch/datasheet/2/216/APTD1608LQBC_D-1102154.pdf | APTD1608LQBC/D | Mouser Electronics | Kingbright | 604-APTD1608LQBCD
26 | Light emitting diode | LED | LED501 LED601 | GREEN | LED_0603_KingBright | 2 | https://www.mouser.ch/datasheet/2/216/APT1608CGCK-24002.pdf | APT1608CGCK | Mouser Electronics | Kingbright | 604-APT1608CGCK
27 | MOSFET Dual P-CH NexFET Pwr MOSFET | CSD75207W15 | Q601 | CSD75207W15 | Texas_DSBGA-9_1.62x1.58mm_Layout3x3_P0.5mm | 1 | https://www.ti.com/lit/ds/symlink/csd75207w15.pdf?ts=1743083254353 | CSD75207W15 | Mouser Electronics | Texas Instruments | 595-CSD75207W15
28 | 20V, N ch NexFET MOSFET, dual common drain LGA 1.35x1.35, 24mOhm | CSD85302L | Q502 | CSD85302L | CSD85302L | 1 | http://www.ti.com/lit/ds/symlink/csd85302l.pdf | CSD85302L | Mouser Electronics | Texas Instruments | 595-CSD85302L
29 | MOSFETs MOSFT 5.0A 29mOhm 30V 2.5V drv capable | Q_NMOS_Depletion_GSD | Q501 | NMOS IRLML6344TRPBF SOT-23 | SOT-23 | 1 | https://www.mouser.ch/datasheet/2/196/Infineon_IRLML6344_DataSheet_v01_01_EN-3363406.pdf | IRLML6344TRPBF | Mouser Electronics | Infineon Technologies | 942-IRLML6344TRPBF
30 | P-MOSFET transistor, gate/source/drain | Q_PMOS_GSD | Q701 | PMOS SI2365EDS-T1-GE3 | SOT-23-3 | 1 | https://www.vishay.com/docs/63199/si2365eds.pdf | SI2365EDS-T1-GE3 | Mouser Electronics | Vishay Semiconductors | 78-SI2365EDS-T1-GE3
31 | Resistor, small symbol | R_Small | R3002 | 0R 1% | R_0603_1608Metric | 1 | https://www.mouser.ch/ProductDetail/YAGEO/RC0603FR-100RL?qs=gY0y7AQI9SNjcfwXbqIKbg%3D%3D | RC0603FR-100RL | Mouser Electronics | YAGEO | 603-RC0603FR-100RL
32 | Resistor | R_Small | R404 R406 R509 R701 R801 R901 R1203 R1303 R1403 R1503 R1603 R1703 R1803 R1903 R2003 R2103 R2203 R2303 R2403 R2503 R2603 R2703 R2803 R2903 | 100k 1% | R_0402_1005Metric | 24 | https://www.mouser.ch/ProductDetail/Panasonic/ERJ-2RKF1003X?qs=H7k1u0Mp9JQnXoBKdf15Qg%3D%3D | ERJ-2RKF1003X | Mouser Electronics | Panasonic | 667-ERJ-2RKF1003X
33 | Resistor | R_Small | R402 R503 R605 R606 R608 | 10k 1% | R_0402_1005Metric | 5 | https://www.mouser.ch/ProductDetail/KOA-Speer/RK73H1ETTPB1002F?qs=sGAEpiMZZMvdGkrng054t65cMycmke1dK22GtXiM9hM%3D | RK73H1ETTPB1002F | Mouser Electronics | KOA Speer | 660-RK73H1ETTPB1002F
34 | Resistor | R_Small | R604 R607 | 196R 1% | R_0402_1005Metric | 2 | https://www.mouser.ch/ProductDetail/Vishay-Dale/CRCW0402196RFKED?qs=9Aka%2FNDvCXC%2FtFusjSrxBQ%3D%3D | CRCW0402196RFKED | Mouser Electronics | Vishay / Dale | 71-CRCW0402196RFKED
35 | Resistor | R_Small | R403 R405 | 22R 1% | R_0402_1005Metric | 2 | https://www.mouser.ch/ProductDetail/KOA-Speer/RK73H1ETTP22R0F | RK73H1ETTP22R0F | Mouser Electronics | KOA Speer | 660-RK73H1ETTP22R0F
36 | Resistor | R_Small | R504 R508 | 2k2 1% | R_0402_1005Metric | 2 | https://www.mouser.ch/ProductDetail/KOA-Speer/RK73H1ETTP2201F?qs=oI046glRuruobG9rEu19Sw%3D%3D | RK73H1ETTP2201F | Mouser Electronics | KOA Speer | 660-RK73H1ETTP2201F
37 | Resistor | R_Small | R401 R501 R505 R601 R1202 R1302 R1402 R1502 R1602 R1702 R1802 R1902 R2002 R2102 R2202 R2302 R2402 R2502 R2602 R2702 R2802 R2902 | 330R 1% | R_0402_1005Metric | 22 | https://www.mouser.ch/ProductDetail/KOA-Speer/RK73H1ETTP3300F?qs=4CJzfoelV6C3hCuuGB%2F5LQ%3D%3D | RK73H1ETTP3300F | Mouser Electronics | KOA Speer | 660-RK73H1ETTP3300F
38 | Resistor | R_Small | R502 R802 R803 R804 R805 R806 R807 R1001 R1002 | 3k 1% | R_0402_1005Metric | 9 | https://www.mouser.ch/ProductDetail/KOA-Speer/RK73H1ETTP3001F?qs=pim%252BJ6MgNfS80Tm8%2FkBkXQ%3D%3D | RK73H1ETTP3001F | Mouser Electronics | KOA Speer | 660-RK73H1ETTP3001F
39 | Resistor | R_Small | R506 R507 | 4M99 1% | R_0402_1005Metric | 2 | https://www.mouser.ch/ProductDetail/KOA-Speer/RK73H1ETTP4994F?qs=v3ImdA%2FOTSQZBfUeBz4Q8A%3D%3D | RK73H1ETTP4994F | Mouser Electronics | KOA Speer | 660-RK73H1ETTP4994F
40 | Resistor | R | R602 R603 | 5k1 1% | R_0402_1005Metric | 2 | https://www.mouser.ch/ProductDetail/KOA-Speer/RK73H1ETTP5101F?qs=0Mn4dg0AsPAhhJD1ZsgV0Q%3D%3D | RK73H1ETTP5101F | Mouser Electronics | KOA Speer | 660-RK73H1ETTP5101F
41 | Resistor | R_Small | R1201 R1301 R1401 R1501 R1601 R1701 R1801 R1901 R2001 R2101 R2201 R2301 R2401 R2501 R2601 R2701 R2801 R2901 | 680R 1% | R_0402_1005Metric | 18 | https://www.mouser.fr/ProductDetail/Vishay-Dale/CRCW0402680RFKEDC?qs=E3Y5ESvWgWPmgUvh1o91RA%3D%3D | CRCW0402680RFKEDC | Mouser Electronics | Vishay / Dale | 71-CRCW0402680RFKEDC
42 | Slide Switches Dual SPDT, ON-ON, slide, J-hook SMD terminals, 100mA @ 6V DC, T&R packaging, non-washable without seal tape | CAS-D20A1 | SW403 | CAS-D20A1 | CAS-D2xx | 1 | https://www.mouser.ch/datasheet/2/972/cas-1628136.pdf | CAS-D20TA1 | Mouser Electronics | Nidec Components | 229-CAS-D20TA1
43 | Tactile Switches SMT Micro Miniature Tactile Switch with 1.9 mm Height Actuator | KMR2_series | SW401 SW402 SW404 SW405 SW406 SW407 | KMR232NG ULC | SW_KMR232NGULCLFS | 6 | https://www.ckswitches.com/media/1479/kmr2.pdf | KMR232NG ULC LFS | Mouser Electronics | C&K | 611-KMR232NGULCLFS
44 | 6-axis, low-power, smart IMU | BMI270 | U1001 | BMI270 | Bosch_LGA-14_3x2.5mm_P0.5mm | 1 | https://www.bosch-sensortec.com/media/boschsensortec/downloads/datasheets/bst-bmi270-ds000.pdf | BMI270 | Mouser Electronics | Bosch Sensortec | 262-BMI270
45 | Voltage and Current Protection for Single-Cell Li-Ion and Li-Polymer Batteries | BQ297xy | U501 | BQ29737DSER | WSON-6_1.5x1.5mm_P0.5mm | 1 | http://www.ti.com/lit/ds/symlink/bq2970.pdf | BQ29737DSER | Mouser Electronics | Texas Instruments | 595-BQ29737DSER
46 | Automotive Highly Integrated Wireless Receiver Qi (WPC v2.0) Compliant Power Supply | BQ51013CQWRHLRQ1 | U601 | BQ51013CQWRHLRQ1 | Texas_VQFN-RHL-20 | 1 | https://www.ti.com/lit/ds/symlink/bq51013c-q1.pdf?ts=1743760265944 | BQ51013CQWRHLRQ1 | Mouser Electronics | Texas Instruments | 595-BQ51013CQWRHLRQ1
47 | Miniature Single-Cell, Fully Integrated Li-Ion, Li-Polymer Charge Management Controllers | MCP73831T-2ACI/MC | U502 | MCP73831T-2ACI/MC | DFN_2x3mm | 1 | https://www.mouser.ch/datasheet/2/268/MCP73831_Family_Data_Sheet_DS20001984H-3441711.pdf | MCP73831T-2ACI/MC | Mouser Electronics | Microchip Technology | 579-MCP73831T-2ACIMC
48 | Low Voltage 4-Channel I2C and SMBus Switch with Reset Function | PCA9546ARGVR | U801 | PCA9546ARGVR | Texas_RSA_VQFN-16-1EP_4x4mm_P0.65mm_EP2.16x2.16mm | 1 | https://www.ti.com/lit/ds/symlink/pca9546a.pdf?ts=1743761042172 | PCA9546ARGVR | Mouser Electronics | Texas Instruments | 595-PCA9546ARGVR
49 | ST Microelectronics STM32WB55VG ARM Cortex Bluetooth Low Energy 5.0, Zigbee and 802.15.4 module, 1 MB Flash, 256kb RAM, Fully integrated BOM | STM32WB5MMG | U401 | STM32WB5MMGH6TR | ST-SiP-LGA-86-11x7.3mm | 1 | https://www.st.com/resource/en/datasheet/stm32wb5mmg.pdf | STM32WB5MMGH6TR | Mouser Electronics | STMicroelectronics | 511-STM32WB5MMGH6TR
50 | 150-nA, Ultralow Power, Supply Voltage Monitor, X2SON-4 | TPS3839DQN | U701 | TPS3839G33DQNR | Texas_X2SON-4_1x1mm_P0.65mm | 1 | http://www.ti.com/lit/ds/sbvs193d/sbvs193d.pdf | TPS3839G33DQNR | Mouser Electronics | Texas Instruments | 595-TPS3839G33DQNR
51 | TPS7A02 Nanopower IQ, 25-nA, 200-mA, Low-Dropout Voltage Regulator With Fast Transient Response | TPS7A02xxxDBVR | U702 | TPS7A0233DBVR | SOT-23-5-TEXAS | 1 | https://www.ti.com/lit/ds/symlink/tps7a02.pdf?ts=1745064259825 | TPS7A0233DBVR | Mouser Electronics | Texas Instruments | 595-TPS7A0233DBVR
Component Groups: | 53
Component Count: | 257
Fitted Components: | 251
Number of PCBs: | 1
Total components: | 251
Schematic Version: | 1.0
Schematic Date: | 2025-04-21
PCB Variant: | default
BoM Date: | 2025-04-24T23:09:42+0200
Schematic Source: | Plume.kicad_sch
KiCad Version: | Eeschema 9.0.0

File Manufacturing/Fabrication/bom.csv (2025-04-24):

Designator | Footprint | Quantity | Value | LCSC Part #
_102, _101, _100, _99, _98, _97, _96, _95, _94, _93, _92, _91, _90, _89, _88, _87, _86, _85, _84, _83, _82, _81, _80, _79, _78, _77, _76, _75, _74, _73, _72, _71, _70, _69, _68, _67, _66, _65, _64, _63, _62, _61, _60, _59, _58, _57, _56, _55, _54, _53, _52, _51, _50, _49, _48, _47, _46, _45, _44, _43, _42, _41, _40, _39, _38, _37, _36, _35, _34, _33, _32, _31, _30, _29, _28, _27, _26, _25, _24, _23, _22, _21, _20, _19, _18, _17, _16, _15, _14, _13, _12, _11, _10, _9, _8, _7, _6, _5, _4, _3, _2, |  | 102
C1001, C1002, C1203, C1303, C1403, C1503, C1603, C1703, C1803, C1903, C2003, C2103, C2203, C2303, C2403, C2503, C2603, C2703, C2803, C2903, C401, C402, C407, C408, C409, C410, C504, C505, C601, C604, C605, C616, C701, C801, C903 | 0402 | 35 | 100n X7R 16V
C1201, C1301, C1401, C1501, C1601, C1701, C1801, C1901, C2001, C2101, C2201, C2301, C2401, C2501, C2601, C2701, C2801, C2901, C602, C617, C618, C702, C703 | 0603 | 23 | 10u X5R 16V
C1202, C1302, C1402, C1502, C1602, C1702, C1802, C1902, C2002, C2102, C2202, C2302, C2402, C2502, C2602, C2702, C2802, C2902 | 0603 | 18 | 100n X7R 50V
C3001, C3002, C3003, C3004 | 0603 | 4 | 1n X7R 1kV
C403, C503, C506 | 0603 | 3 | 4u7 X7R 16V
C501, C502 | 1206 | 2 | 47u X5R 16V
C603, C802 | 0603 | 2 | 1u X7R 16V
C606, C609, C615 | 0402 | 3 | 10n C0G 25V
C607, C613 | 0402 | 2 | 470n X5R 25V
C608, C614 | 0402 | 2 | 22n X7R 25V
C610 | 0402 | 1 | 150n X7R 25V
C611 | 0402 | 1 | 2n2 X7R 25V
C612 | 0402 | 1 | 390pF X7R 25V
C901 | 0603 | 1 | 220n X7R 16V
C902, C904 | 0603 | 2 | 2u2 X7R 16V
D401 | SOT-23-5-TEXAS | 1 | ESDS314
D601 | D_SOD-123FL | 1 | TVS SMF5.0A
D701 | Nexperia_CFP3_SOD-123W | 1 | Schottky 1N5819W
D901 | INPI22TAT5R5G5B | 1 | IN-PI22TAT5R5G5B
IC1201, IC1301, IC1401, IC1501, IC1601, IC1701, IC1801, IC1901, IC2001, IC2101, IC2201, IC2301, IC2401, IC2501, IC2601, IC2701, IC2801, IC2901 | WQFN-16-1EP_3x3mm_P0.5mm_EP1.68x1.68mm_ThermalVias | 18 | DRV8214RTER
IC901 | SOT-553 | 1 | SN74AHCT1G125DRLR
IC902 | WSON-6-1EP_2x2mm_P0.65mm_EP1x1.6mm | 1 | REG71050DRVR
J502 | CONN_S2B-PH-SM4-TB_JST | 1 | S2B-PH-SM4-TB
J602 | USB4125-GF-A | 1 | USB_C_Receptacle_PowerOnly_6P
LED1201, LED1301, LED1401, LED1501, LED1601, LED1701, LED1801, LED1901, LED2001, LED2101, LED2201, LED2301, LED2401, LED2501, LED2601, LED2701, LED2801, LED2901 | LED_0603_KingBright | 18 | BLUE
LED501, LED601 | LED_0603_KingBright | 2 | GREEN
Q501 | SOT-23 | 1 | NMOS IRLML6344TRPBF SOT-23
Q502 | CSD85302L | 1 | CSD85302L
Q601 | Texas_DSBGA-9_1.62x1.58mm_Layout3x3_P0.5mm | 1 | CSD75207W15
Q701 | SOT-23-3 | 1 | PMOS SI2365EDS-T1-GE3
R1001, R1002, R502, R802, R803, R804, R805, R806, R807 | 0402 | 9 | 3k 1%
R1201, R1301, R1401, R1501, R1601, R1701, R1801, R1901, R2001, R2101, R2201, R2301, R2401, R2501, R2601, R2701, R2801, R2901 | 0402 | 18 | 680R 1%
R1202, R1302, R1402, R1502, R1602, R1702, R1802, R1902, R2002, R2102, R2202, R2302, R2402, R2502, R2602, R2702, R2802, R2902, R401, R501, R505, R601 | 0402 | 22 | 330R 1%
R1203, R1303, R1403, R1503, R1603, R1703, R1803, R1903, R2003, R2103, R2203, R2303, R2403, R2503, R2603, R2703, R2803, R2903, R404, R406, R509, R701, R801, R901 | 0402 | 24 | 100k 1%
R3001, R3002, R3003, R3004 | 0603 | 4 | 0R 1%
R402, R503, R605, R606, R608 | 0402 | 5 | 10k 1%
R403, R405 | 0402 | 2 | 22R 1%
R504, R508 | 0402 | 2 | 2k2 1%
R506, R507 | 0402 | 2 | 4M99 1%
R602, R603 | 0402 | 2 | 5k1 1%
R604, R607 | 0402 | 2 | 196R 1%
SW401, SW402, SW404, SW405, SW406, SW407 | SW_KMR232NGULCLFS | 6 | KMR232NG ULC
SW403 | CAS-D2xx | 1 | CAS-D20A1
U1001 | Bosch_LGA-14_3x2.5mm_P0.5mm | 1 | BMI270
U401 | ST-SiP-LGA-86-11x7.3mm | 1 | STM32WB5MMGH6TR
U501 | WSON-6_1.5x1.5mm_P0.5mm | 1 | BQ29737DSER
U502 | DFN_2x3mm | 1 | MCP73831T-2ACI/MC
U601 | Texas_VQFN-RHL-20 | 1 | BQ51013CQWRHLRQ1
U701 | Texas_X2SON-4_1x1mm_P0.65mm | 1 | TPS3839G33DQNR
U702 | SOT-23-5-TEXAS | 1 | TPS7A0233DBVR
U801 | Texas_RSA_VQFN-16-1EP_4x4mm_P0.65mm_EP2.16x2.16mm | 1 | PCA9546ARGVR

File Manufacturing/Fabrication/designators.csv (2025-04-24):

:102
C1001:1
C1002:1
C1201:1
C1202:1
C1203:1
C1301:1
C1302:1
C1303:1
C1401:1
C1402:1
C1403:1
C1501:1
C1502:1
C1503:1
C1601:1
C1602:1
C1603:1
C1701:1
C1702:1
C1703:1
C1801:1
C1802:1
C1803:1
C1901:1
C1902:1
C1903:1
C2001:1
C2002:1
C2003:1
C2101:1
C2102:1
C2103:1
C2201:1
C2202:1
C2203:1
C2301:1
C2302:1
C2303:1
C2401:1
C2402:1
C2403:1
C2501:1
C2502:1
C2503:1
C2601:1
C2602:1
C2603:1
C2701:1
C2702:1
C2703:1
C2801:1
C2802:1
C2803:1
C2901:1
C2902:1
C2903:1
C3001:1
C3002:1
C3003:1
C3004:1
C401:1
C402:1
C403:1
C407:1
C408:1
C409:1
C410:1
C501:1
C502:1
C503:1
C504:1
C505:1
C506:1
C601:1
C602:1
C603:1
C604:1
C605:1
C606:1
C607:1
C608:1
C609:1
C610:1
C611:1
C612:1
C613:1
C614:1
C615:1
C616:1
C617:1
C618:1
C701:1
C702:1
C703:1
C801:1
C802:1
C901:1
C902:1
C903:1
C904:1
D401:1
D601:1
D701:1
D901:1
FID3001:1
FID3002:1
FID3003:1
FID3004:1
FID3005:1
FID3006:1
FID3007:1
FID3008:1
H3001:1
H3002:1
H3003:1
H3004:1
H3005:1
H3006:1
H3007:1
H3008:1
IC1201:1
IC1301:1
IC1401:1
IC1501:1
IC1601:1
IC1701:1
IC1801:1
IC1901:1
IC2001:1
IC2101:1
IC2201:1
IC2301:1
IC2401:1
IC2501:1
IC2601:1
IC2701:1
IC2801:1
IC2901:1
IC901:1
IC902:1
J1101:1
J1102:1
J1103:1
J1104:1
J1105:1
J1106:1
J401:1
J402:1
J403:1
J404:1
J405:1
J406:1
J501:1
J502:1
J503:1
J601:1
J602:1
J603:1
J604:1
J605:1
JP1001:1
JP801:1
KIBUZZARD-67FBF429:1
KIBUZZARD-67FBF4BC:1
KIBUZZARD-67FBF564:1
KIBUZZARD-67FBF56D:1
KIBUZZARD-67FD26D2:1
KIBUZZARD-67FD2784:1
KIBUZZARD-67FD279F:1
KIBUZZARD-67FD2926:1
KIBUZZARD-67FD2947:1
KIBUZZARD-67FD2980:1
KIBUZZARD-67FD2990:1
KIBUZZARD-67FD299D:1
KIBUZZARD-67FD29AC:1
KIBUZZARD-67FD29EA:1
KIBUZZARD-67FD29F6:1
KIBUZZARD-67FD2A58:1
KIBUZZARD-67FD2AAD:1
KIBUZZARD-67FD2AC2:1
KIBUZZARD-67FD2B0D:1
KIBUZZARD-67FD2B35:1
KIBUZZARD-67FD2B62:1
KIBUZZARD-67FD2C07:1
KIBUZZARD-67FD2C0F:1
KIBUZZARD-67FD2C7C:2
KIBUZZARD-67FD2CA8:1
KIBUZZARD-67FD2CD5:1
KIBUZZARD-67FD4094:1
KIBUZZARD-67FD40A9:1
KIBUZZARD-67FD4986:1
KIBUZZARD-67FD49AB:1
KIBUZZARD-67FD49C3:1
KIBUZZARD-67FD49DC:1
KIBUZZARD-67FD49F9:2
KIBUZZARD-67FD4A4D:1
KIBUZZARD-67FD4A6E:1
KIBUZZARD-67FD4ADF:1
KIBUZZARD-67FD4B4D:1
KIBUZZARD-67FD4BA6:1
KIBUZZARD-67FD4BFC:1
KIBUZZARD-67FD4C4E:1
KIBUZZARD-67FD4C83:1
KIBUZZARD-67FD4E82:2
KIBUZZARD-67FD4E8D:2
KIBUZZARD-67FD4ED6:2
KIBUZZARD-67FD4F32:2
KIBUZZARD-67FD5353:1
KIBUZZARD-67FD54FE:1
KIBUZZARD-67FD555E:1
KIBUZZARD-67FD5597:1
KIBUZZARD-67FD563C:1
KIBUZZARD-68021211:1
KIBUZZARD-6804C593:1
KIBUZZARD-6804C5B8:1
KIBUZZARD-6806100C:1
KIBUZZARD-680671DA:1
KIBUZZARD-6809FB86:1
KIBUZZARD-6809FBC0:1
LED1201:1
LED1301:1
LED1401:1
LED1501:1
LED1601:1
LED1701:1
LED1801:1
LED1901:1
LED2001:1
LED2101:1
LED2201:1
LED2301:1
LED2401:1
LED2501:1
LED2601:1
LED2701:1
LED2801:1
LED2901:1
LED501:1
LED601:1
Q501:1
Q502:1
Q601:1
Q701:1
R1001:1
R1002:1
R1201:1
R1202:1
R1203:1
R1301:1
R1302:1
R1303:1
R1401:1
R1402:1
R1403:1
R1501:1
R1502:1
R1503:1
R1601:1
R1602:1
R1603:1
R1701:1
R1702:1
R1703:1
R1801:1
R1802:1
R1803:1
R1901:1
R1902:1
R1903:1
R2001:1
R2002:1
R2003:1
R2101:1
R2102:1
R2103:1
R2201:1
R2202:1
R2203:1
R2301:1
R2302:1
R2303:1
R2401:1
R2402:1
R2403:1
R2501:1
R2502:1
R2503:1
R2601:1
R2602:1
R2603:1
R2701:1
R2702:1
R2703:1
R2801:1
R2802:1
R2803:1
R2901:1
R2902:1
R2903:1
R3001:1
R3002:1
R3003:1
R3004:1
R401:1
R402:1
R403:1
R404:1
R405:1
R406:1
R501:1
R502:1
R503:1
R504:1
R505:1
R506:1
R507:1
R508:1
R509:1
R601:1
R602:1
R603:1
R604:1
R605:1
R606:1
R607:1
R608:1
R701:1
R801:1
R802:1
R803:1
R804:1
R805:1
R806:1
R807:1
R901:1
SW401:1
SW402:1
SW403:1
SW404:1
SW405:1
SW406:1
SW407:1
TP1001:1
TP1002:1
TP1101:1
TP1102:1
TP1103:1
TP1104:1
TP1105:1
TP1106:1
TP1201:1
TP1202:1
TP1203:1
TP1204:1
TP1205:1
TP1206:1
TP1301:1
TP1302:1
TP1303:1
TP1304:1
TP1305:1
TP1306:1
TP1401:1
TP1402:1
TP1403:1
TP1404:1
TP1405:1
TP1406:1
TP1501:1
TP1502:1
TP1503:1
TP1504:1
TP1505:1
TP1506:1
TP1601:1
TP1602:1
TP1603:1
TP1604:1
TP1605:1
TP1606:1
TP1701:1
TP1702:1
TP1703:1
TP1704:1
TP1705:1
TP1706:1
TP1801:1
TP1802:1
TP1803:1
TP1804:1
TP1805:1
TP1806:1
TP1901:1
TP1902:1
TP1903:1
TP1904:1
TP1905:1
TP1906:1
TP2001:1
TP2002:1
TP2003:1
TP2004:1
TP2005:1
TP2006:1
TP2101:1
TP2102:1
TP2103:1
TP2104:1
TP2105:1
TP2106:1
TP2201:1
TP2202:1
TP2203:1
TP2204:1
TP2205:1
TP2206:1
TP2301:1
TP2302:1
TP2303:1
TP2304:1
TP2305:1
TP2306:1
TP2401:1
TP2402:1
TP2403:1
TP2404:1
TP2405:1
TP2406:1
TP2501:1
TP2502:1
TP2503:1
TP2504:1
TP2505:1
TP2506:1
TP2601:1
TP2602:1
TP2603:1
TP2604:1
TP2605:1
TP2606:1
TP2701:1
TP2702:1
TP2703:1
TP2704:1
TP2705:1
TP2706:1
TP2801:1
TP2802:1
TP2803:1
TP2804:1
TP2805:1
TP2806:1
TP2901:1
TP2902:1
TP2903:1
TP2904:1
TP2905:1
TP2906:1
TP401:1
TP402:1
TP403:1
TP404:1
TP405:1
TP406:1
TP407:1
TP408:1
TP501:1
TP502:1
TP503:1
TP504:1
TP505:1
TP506:1
TP507:1
TP508:1
TP509:1
TP601:1
TP602:1
TP603:1
TP604:1
TP701:1
TP702:1
TP703:1
TP704:1
TP801:1
TP901:1
TP902:1
TP903:1
TP904:1
U1001:1
U401:1
U501:1
U502:1
U601:1
U701:1
U702:1
U801:1

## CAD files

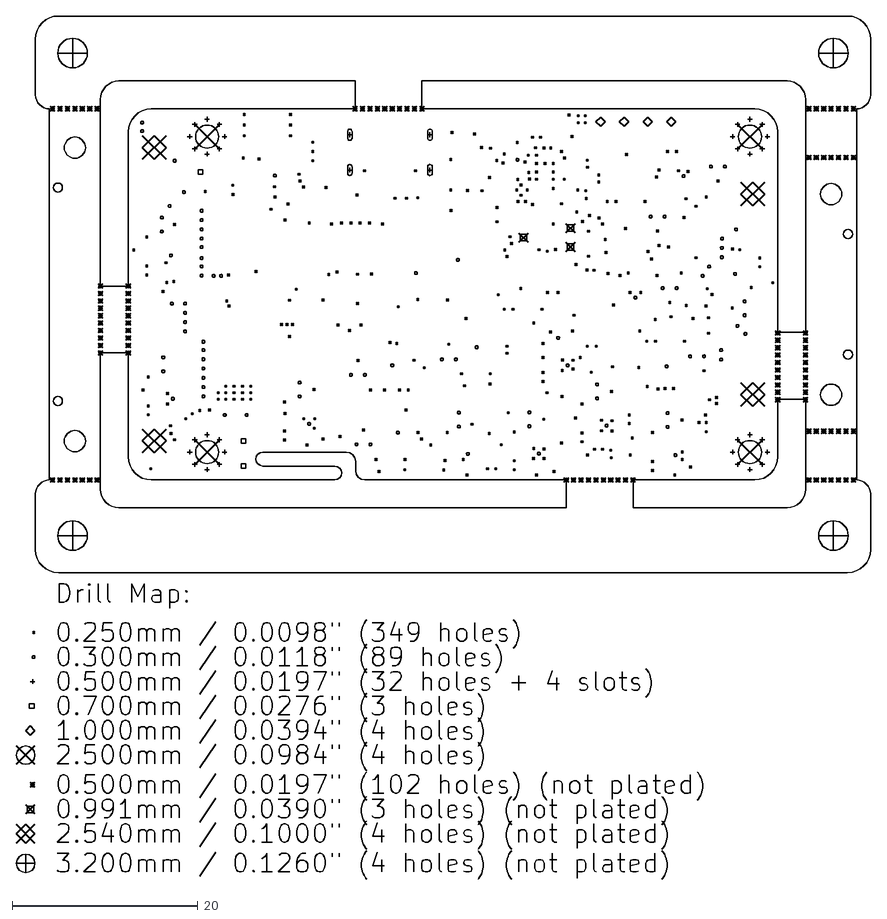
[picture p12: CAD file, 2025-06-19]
Manufacturing/Fabrication/Gerbers/Plume-drl_map.dxf
92.1 x 93.0

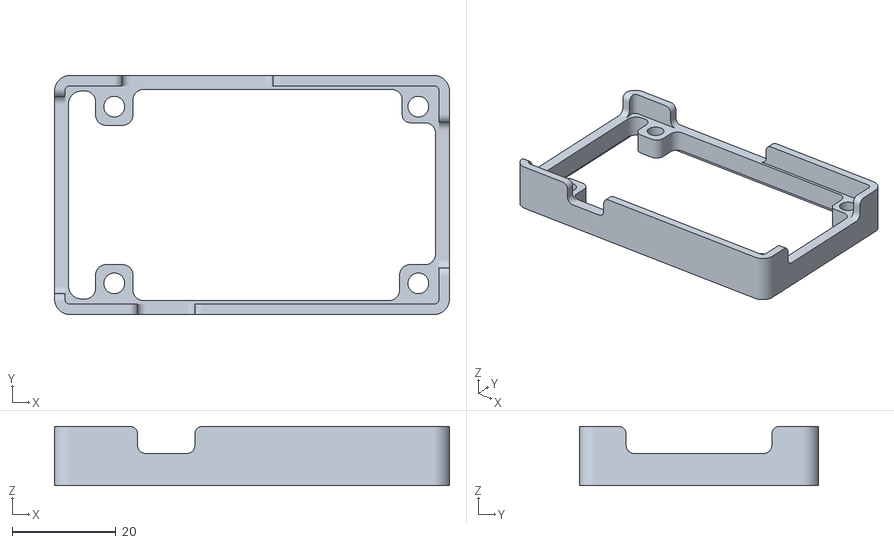
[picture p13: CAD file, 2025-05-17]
STEP_BLENDER_STL/bottom_cover.stl
76.0 x 46.0 x 11.4

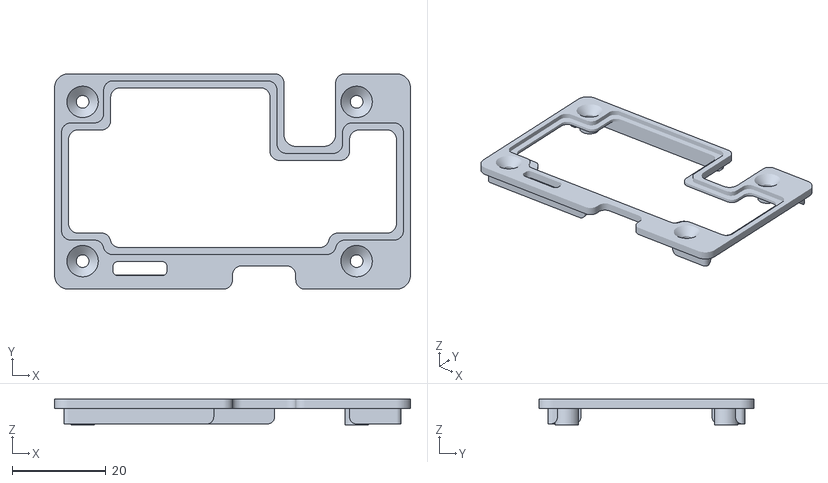
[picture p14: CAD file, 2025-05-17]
STEP_BLENDER_STL/top_cover.stl
76.0 x 46.0 x 5.50

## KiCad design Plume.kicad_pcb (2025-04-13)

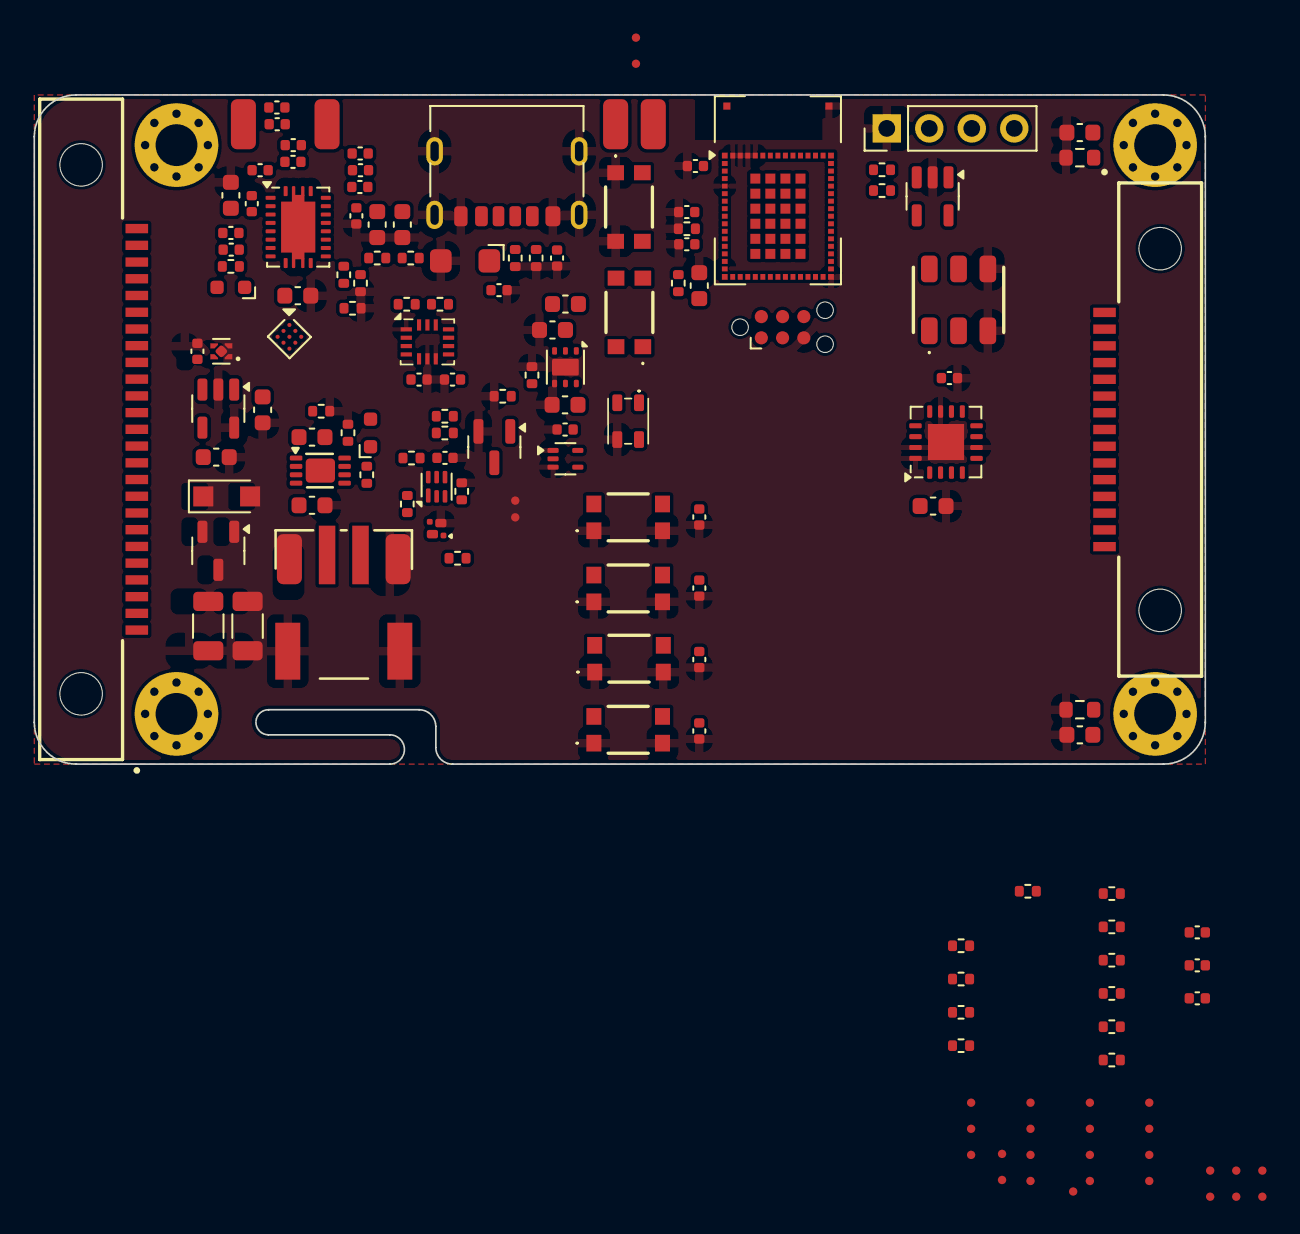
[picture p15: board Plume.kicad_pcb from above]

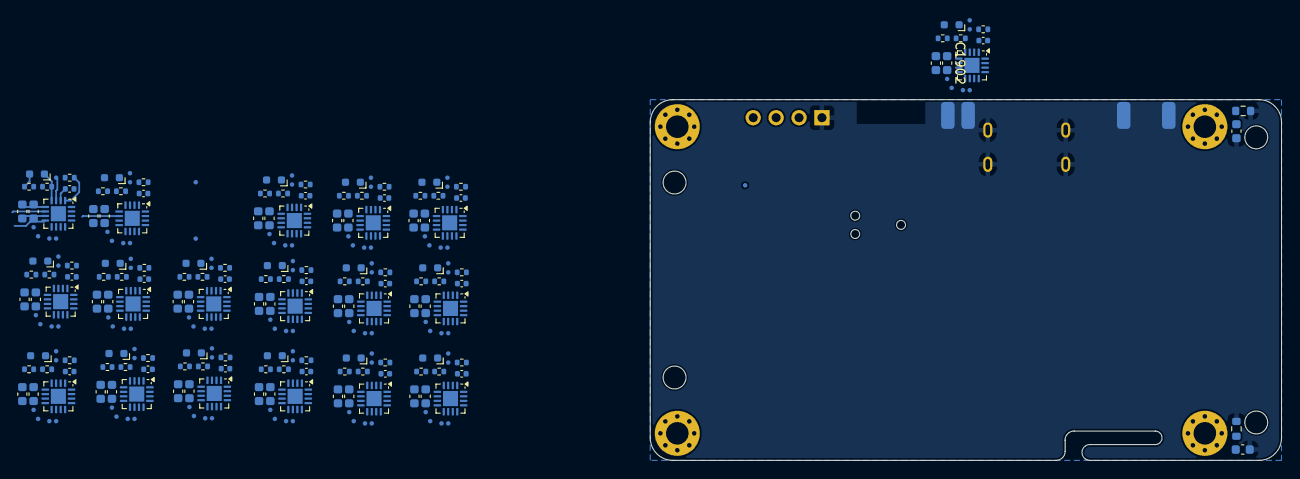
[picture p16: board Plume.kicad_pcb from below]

Board: 6 copper layers, 70.0 x 40.0 mm, 418 parts (262 on the bottom side), 203 nets.

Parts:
C401, C402, C404, C405, C406, C407, C502, C503, C601, C604, C605, C616, C701, C802, C1003, C1103, C1203, C1303, C1403, C1503, C1603, C1703, C1803, C1903, C2003, C2103, C2203, C2303, C2403, C2503, C2603, C2703, C2803, C2805, C2806: 100n X7R 16V; C_0402_1005Metric
C403, C501, C504: 4u7 X7R 16V; C_0603_1608Metric
C408, C409, C410: 3p3 C0G 50V; C_0402_1005Metric
C506, C507: 47u X5R 16V; C_1206_3216Metric
C602, C617, C618, C703, C704, C1001, C1101, C1201, C1301, C1401, C1501, C1601, C1701, C1801, C1901, C2001, C2101, C2201, C2301, C2401, C2501, C2601, C2701: 10u X5R 16V; C_0603_1608Metric
C603, C801: 1u X7R 16V; C_0603_1608Metric
C606, C609, C615: 10n C0G 25V; C_0402_1005Metric
C607, C613: 470n X5R 25V; C_0402_1005Metric
C608, C614: 22n X7R 25V; C_0402_1005Metric
C610: 150n X7R 25V; C_0402_1005Metric
C611: 2n2 X7R 25V; C_0402_1005Metric
C612: 390pF X7R 25V; C_0402_1005Metric
C1002, C1102, C1202, C1302, C1402, C1502, C1602, C1702, C1802, C1902, C2002, C2102, C2202, C2302, C2402, C2502, C2602, C2702: 100n X7R 50V; C_0603_1608Metric
C2801: 220n X7R 16V; C_0603_1608Metric
C2802, C2804: 2u2 X7R 16V; C_0603_1608Metric
C2901, C2902, C2903, C2904: 1n X7R 1kV; C_0603_1608Metric
D401: ESDS314; SOT-23-5
D601: TVS SMF5.0A; D_SOD-123FL
D701: Schottky 1N5819W; Nexperia_CFP3_SOD-123W
D2801: IN-PI22TAT5R5G5B; INPI22TAT5R5G5B
H2901, H2902, H2903, H2904: M2.5 (2.7mm); MountingHole_2.5mm_Pad_Via
IC1001, IC1101, IC1201, IC1301, IC1401, IC1501, IC1601, IC1701, IC1801, IC1901, IC2001, IC2101, IC2201, IC2301, IC2401, IC2501, IC2601, IC2701: DRV8214RTER; WQFN-16-1EP_3x3mm_P0.5mm_EP1.68x1.68mm_ThermalVias
IC2801: SN74AHCT1G125DRLR; SOT-553
IC2802: REG71050DRVT; WSON-6-1EP_2x2mm_P0.65mm_EP1x1.6mm
J401: Solder Holes 4x1 2.54mm 22AWG; PinHeader_1x04_P2.54mm_Vertical
J402: Conn_ARM_SWD_TagConnect_TC2030-NL; Tag-Connect_TC2030-IDC-NL_2x03_P1.27mm_Vertical
J403, J404, J405, J406, J407, J408, J602, J603, J604, J605: Solder Wire Pad 1,5x3mm; SolderWirePad_SMD_1,5x3mm
J501: S2B-PH-SM4-TB; CONN_S2B-PH-SM4-TB_JST
J601: USB_C_Receptacle_PowerOnly_6P; USB4125-GF-A
J901: SEI-125-02-GF-S-M-AT; SAMTEC_SEI-125-02-GF-S-M-AT
J902: SEI-115-02-GF-S-M-AT; SAMTEC_SEI-115-02-GF-S-M-AT
LED501, LED502: GREEN; KingBright_LED_0603
LED1001, LED1101, LED1201, LED1301, LED1401, LED1501, LED1601, LED1701, LED1801, LED1901, LED2001, LED2101, LED2201, LED2301, LED2401, LED2501, LED2601, LED2701: BLUE; KingBright_LED_0603
Q501: NMOS IRLML6344TRPBF SOT-23; SOT-23
Q502: CSD85302L
Q601: CSD75207W15; Texas_DSBGA-9_1.62x1.58mm_Layout3x3_P0.5mm
Q701: PMOS SI2365EDS-T1-GE3; SOT-23-3
R401, R501, R505, R510, R1002, R1102, R1202, R1302, R1402, R1502, R1602, R1702, R1802, R1902, R2002, R2102, R2202, R2302, R2402, R2502, R2602, R2702: 330R 1%; R_0402_1005Metric
R403, R404: 22R 1%; R_0402_1005Metric
R502, R802, R803, R804, R805, R806, R807, R808, R809, R810, R811, R812, R813: 3k 1%; R_0402_1005Metric
R503, R605, R606, R608, R609: 10k 1%; R_0402_1005Metric
R504, R508: 2k2 1%; R_0402_1005Metric
R506, R507: 4M99 1%; R_0402_1005Metric
R509, R701, R801, R1003, R1103, R1203, R1303, R1403, R1503, R1603, R1703, R1803, R1903, R2003, R2103, R2203, R2303, R2403, R2503, R2603, R2703, R2801: 100k 1%; R_0402_1005Metric
R602, R603: 5k1 1%; R_0402_1005Metric
R604, R607: 196R 1%; R_0402_1005Metric
R1001, R1101, R1201, R1301, R1401, R1501, R1601, R1701, R1801, R1901, R2001, R2101, R2201, R2301, R2401, R2501, R2601, R2701: 680R 1%; R_0402_1005Metric
R2901, R2902, R2903, R2904: 0R 1%; R_0603_1608Metric
SW401, SW402, SW404, SW405, SW406, SW407: KMR232NG ULC; KMR232NGULCLFS
SW403: CAS-D20A1; CAS-D2xx
TP401: BUTTON1; TestPoint_Pad_D0.5mm_Back
TP402: BUTTON2; TestPoint_Pad_D0.5mm_Back
TP403: BUTTON3; TestPoint_Pad_D0.5mm_Back
TP404: BUTTON4; TestPoint_Pad_D0.5mm_Back
TP405: SWITCH1; TestPoint_Pad_D0.5mm_Back
TP406: SWITCH2; TestPoint_Pad_D0.5mm_Back
TP501: COUT; TestPoint_Pad_D0.5mm_Back
TP502: DOUT; TestPoint_Pad_D0.5mm_Back
TP503: CHARGE_STATUS; TestPoint_Pad_D0.5mm_Back
TP504: BAT_SENSE_EN; TestPoint_Pad_D0.5mm_Back
TP505: BAT_SENSE; TestPoint_Pad_D0.5mm_Back
TP506: -VBAT; TestPoint_Pad_D0.5mm_Back
TP507: VBAT; TestPoint_Pad_D0.5mm_Back
TP601: +VBUS; TestPoint_Pad_D0.5mm_Back
TP602: +VCHARGE; TestPoint_Pad_D0.5mm_Back
TP603: ~{AD_EN}; TestPoint_Pad_D0.5mm_Back
TP604: ~{CHG}; TestPoint_Pad_D0.5mm_Back
TP701: 3V3_EN; TestPoint_Pad_D0.5mm_Back
TP702, TP802: +3V3; TestPoint_Pad_D0.5mm_Back
TP703: +VDD; TestPoint_Pad_D0.5mm_Back
TP801: MUX_RESET; TestPoint_Pad_D0.5mm_Back
TP901: nSLEEP_FRONT; TestPoint_Pad_D0.5mm_Back
TP902: nSLEEP_REAR; TestPoint_Pad_D0.5mm_Back
TP1001, TP1101, TP1201, TP1301, TP1401, TP1501, TP1601, TP1701, TP1801, TP1901, TP2001, TP2101, TP2201, TP2301, TP2401, TP2501, TP2601, TP2701: nFAULT; TestPoint_Pad_D0.5mm_Back
TP1002, TP1102, TP1202, TP1302, TP1402, TP1502, TP1602, TP1702, TP1802, TP1902, TP2002, TP2102, TP2202, TP2302, TP2402, TP2502, TP2602, TP2702: RC_OUT; TestPoint_Pad_D0.5mm_Back
TP1003, TP1103, TP1203, TP1303, TP1403, TP1503, TP1603, TP1703, TP1803, TP1903, TP2003, TP2103, TP2203, TP2303, TP2403, TP2503, TP2603, TP2703: OUT1; TestPoint_Pad_D0.5mm_Back
TP1004, TP1104, TP1204, TP1304, TP1404, TP1504, TP1604, TP1704, TP1804, TP1904, TP2004, TP2104, TP2204, TP2304, TP2404, TP2504, TP2604, TP2704: OUT2; TestPoint_Pad_D0.5mm_Back
TP1005, TP1105, TP1205, TP1305, TP1405, TP1505, TP1605, TP1705, TP1805, TP1905, TP2005, TP2105, TP2205, TP2305, TP2405, TP2505, TP2605, TP2705: A0; TestPoint_Pad_D0.5mm_Back
TP1006, TP1106, TP1206, TP1306, TP1406, TP1506, TP1606, TP1706, TP1806, TP1906, TP2006, TP2106, TP2206, TP2306, TP2406, TP2506, TP2606, TP2706: A1; TestPoint_Pad_D0.5mm_Back
TP2801: 5V_ENABLE; TestPoint_Pad_D0.5mm_Back
TP2802: DIN_3V3; TestPoint_Pad_D0.5mm_Back
TP2803, TP2807: INT1; TestPoint_Pad_D0.5mm_Back
TP2804, TP2808: INT2; TestPoint_Pad_D0.5mm_Back
U401: STM32WB5MMGH6TR; ST-SiP-LGA-86-11x7.3mm
U501: BQ29737DSER; WSON-6_1.5x1.5mm_P0.5mm
U502: MCP73831T-2ACI/MC; DFN_2x3mm
U601: BQ51013CQWRHLRQ1; Texas_VQFN-RHL-20
U701: TPS3839G33DQNR; Texas_X2SON-4_1x1mm_P0.65mm
U702: TPS7A0233DBVR; SOT-23-5
U801: PCA9546ARGVR; Texas_RSA_VQFN-16-1EP_4x4mm_P0.65mm_EP2.16x2.16mm
U3202: BMI270; Bosch_LGA-14_3x2.5mm_P0.5mm

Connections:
+3V3: C403.1, C703.1, C801.1, C802.1, C2804.1, C2805.1, C2806.1, D401.5 (I/O4), IC1201.10 (A0), IC1501.10 (A0), IC1601.9 (A1), IC1701.9 (A1), IC1801.9 (A1), IC1801.10 (A0), IC2101.10 (A0), IC2401.10 (A0), IC2501.9 (A1), IC2601.9 (A1), IC2701.9 (A1), IC2701.10 (A0), IC2802.2 (V_IN), J401.4, J402.1 (VCC), R801.1, R802.1, R803.1, R804.1, R805.1, R806.1, R807.1, R808.1, R809.1, R810.1, R811.1, R812.1, R813.1, R1002.1, R1003.1, R1102.1, R1103.1, R1202.1, R1203.1, R1302.1, R1303.1, R1402.1, R1403.1, R1502.1, R1503.1, R1602.1, R1603.1, R1702.1, R1703.1, R1802.1, R1803.1, R1902.1, R1903.1, R2002.1, R2003.1, R2102.1, R2103.1, R2202.1, R2203.1, R2302.1, R2303.1, R2402.1, R2403.1, R2502.1, R2503.1, R2602.1, R2603.1, R2702.1, R2703.1, SW401.2, SW401.3, SW403.1, SW403.4, TP702.1, TP802.1, TP1205.1, TP1505.1, TP1606.1, TP1706.1, TP1805.1, TP1806.1, TP2105.1, TP2405.1, TP2506.1, TP2606.1, TP2705.1, TP2706.1, U401.4 (VREF), U401.6 (VDDA), U401.15 (VBAT), U401.17 (VDDSMPS), U401.32 (VDDUSB), U702.1 (OUT), U801.14 (VCC), U3202.5 (VDDIO), U3202.8 (VDD), U3202.12 (CSB)
+VBUS: C603.1, C604.1, C605.1, D601.1 (K), J601.A9 (VBUS), J601.B9 (VBUS), Q601.2 (D1), Q601.3 (D1), Q601.6 (D1), TP601.1, U601.9 (AD)
/Project Architecture/Logic - I2C Mux/I2C1_SCL: R803.2, U401.14 (PB8), U801.12 (SCL)
/Project Architecture/Logic - I2C Mux/I2C1_SDA: R802.2, U401.11 (PB9), U801.13 (SDA)
/Project Architecture/Logic - I2C Mux/MUX_RESET: R801.2, TP801.1, U801.1 (RESET)
/Project Architecture/Logic - I2C Mux/SC0: R804.2, U801.3 (SC0)
/Project Architecture/Logic - I2C Mux/SC1: R810.2, U801.5 (SC1)
/Project Architecture/Logic - I2C Mux/SC2: R809.2, U801.7 (SD2)
/Project Architecture/Logic - I2C Mux/SC3: R807.2, U801.9 (SD3)
/Project Architecture/Logic - I2C Mux/SD0: R805.2, U801.2 (SD0)
/Project Architecture/Logic - I2C Mux/SD1: R811.2, U801.4 (SD1)
/Project Architecture/Logic - I2C Mux/SD2: R808.2, U801.8 (SC2)
/Project Architecture/Logic - I2C Mux/SD3: R806.2, U801.10 (SC3)
/Project Architecture/MCU - Unit/5V_ENABLE: IC2802.5 (ENABLE), R2801.1, TP2801.1, U401.8 (PC2)
/Project Architecture/MCU - Unit/BAT_SENSE: C502.2, R502.2, R503.1, TP505.1, U401.2 (PA1)
/Project Architecture/MCU - Unit/BAT_SENSE_EN: Q501.1 (G), R509.1, TP504.1, U401.3 (PA0)
/Project Architecture/MCU - Unit/BOOT0: C401.1, R401.2, R609.2, U401.13 (PH3-BOOT0)
/Project Architecture/MCU - Unit/BOOT0_B: R401.1, SW401.1, SW401.4
/Project Architecture/MCU - Unit/BUTTON1: C404.1, SW404.2, SW404.3, TP401.1, U401.18 (PB7)
/Project Architecture/MCU - Unit/BUTTON2: C405.1, SW405.2, SW405.3, TP402.1, U401.19 (PB5)
/Project Architecture/MCU - Unit/BUTTON3: C406.1, SW406.2, SW406.3, TP403.1, U401.20 (PB4)
/Project Architecture/MCU - Unit/BUTTON4: C407.1, SW407.2, SW407.3, TP404.1, U401.22 (PC10)
/Project Architecture/MCU - Unit/CHARGE_STATUS: R505.2, TP503.1, U502.5 (STAT)
/Project Architecture/MCU - Unit/DIN_3V3: IC2801.2 (A), TP2802.1, U401.7 (PC3)
/Project Architecture/MCU - Unit/EN1: U401.56 (PA3), U601.10 (EN1)
/Project Architecture/MCU - Unit/EN2: U401.1 (PA2), U601.11 (EN2)
/Project Architecture/MCU - Unit/I2C3_SCL: J403.1, J408.1, R813.2, U401.12 (PC0), U3202.13 (SCx)
/Project Architecture/MCU - Unit/I2C3_SDA: J404.1, J407.1, R812.2, U401.9 (PC1), U3202.14 (SDx)
/Project Architecture/MCU - Unit/SWCLK: J402.4 (SWCLK), U401.26 (PA14)
/Project Architecture/MCU - Unit/SWDIO: J402.2 (SWDIO), U401.25 (PA13)
/Project Architecture/MCU - Unit/SWITCH1: SW403.5, TP405.1
/Project Architecture/MCU - Unit/SWITCH2: SW403.2, TP406.1
/Project Architecture/MCU - Unit/SWO: J402.6 (SWO), U401.21 (PB3)
/Project Architecture/MCU - Unit/USART1_RX: R404.1, U401.28 (PA10)
/Project Architecture/MCU - Unit/USART1_RX_C: D401.1 (I/O1), D401.3 (I/O2), J401.2, J401.3, R403.2, R404.2
/Project Architecture/MCU - Unit/USART1_TX: R403.1, U401.51 (PA9)
/Project Architecture/MCU - Unit/nFault0: IC1001.4 (nFAULT), LED1001.1 (K), R1003.2, TP1001.1, U401.50 (PA8)
/Project Architecture/MCU - Unit/nFault1: IC1101.4 (nFAULT), LED1101.1 (K), R1103.2, TP1101.1, U401.49 (PC4)
/Project Architecture/MCU - Unit/nFault2: IC1201.4 (nFAULT), LED1201.1 (K), R1203.2, TP1201.1, U401.48 (PB2)
/Project Architecture/MCU - Unit/nFault3: C408.1, IC1301.4 (nFAULT), LED1301.1 (K), R1303.2, TP1301.1, U401.47 (PB10)
/Project Architecture/MCU - Unit/nFault4: C409.1, IC1401.4 (nFAULT), LED1401.1 (K), R1403.2, TP1401.1, U401.46 (PB11)
/Project Architecture/MCU - Unit/nFault5: C410.1, IC1501.4 (nFAULT), LED1501.1 (K), R1503.2, TP1501.1, U401.45 (PC5)
/Project Architecture/MCU - Unit/nFault6: IC1601.4 (nFAULT), LED1601.1 (K), R1603.2, TP1601.1, U401.44 (PB0)
/Project Architecture/MCU - Unit/nFault7: IC1701.4 (nFAULT), LED1701.1 (K), R1703.2, TP1701.1, U401.43 (PB1)
/Project Architecture/MCU - Unit/nFault8: IC1801.4 (nFAULT), LED1801.1 (K), R1803.2, TP1801.1, U401.42 (PE4)
/Project Architecture/MCU - Unit/nFault9: IC1901.4 (nFAULT), LED1901.1 (K), R1903.2, TP1901.1, U401.41 (PB12)
/Project Architecture/MCU - Unit/nFault10: IC2001.4 (nFAULT), LED2001.1 (K), R2003.2, TP2001.1, U401.40 (PC13)
/Project Architecture/MCU - Unit/nFault11: IC2101.4 (nFAULT), LED2101.1 (K), R2103.2, TP2101.1, U401.39 (PB6)
/Project Architecture/MCU - Unit/nFault12: IC2201.4 (nFAULT), LED2201.1 (K), R2203.2, TP2201.1, U401.38 (PB15)
/Project Architecture/MCU - Unit/nFault13: IC2301.4 (nFAULT), LED2301.1 (K), R2303.2, TP2301.1, U401.37 (PB14)
/Project Architecture/MCU - Unit/nFault14: IC2401.4 (nFAULT), LED2401.1 (K), R2403.2, TP2401.1, U401.36 (PC6)
/Project Architecture/MCU - Unit/nFault15: IC2501.4 (nFAULT), LED2501.1 (K), R2503.2, TP2501.1, U401.35 (PB13)
/Project Architecture/MCU - Unit/nFault16: IC2601.4 (nFAULT), LED2601.1 (K), R2603.2, TP2601.1, U401.34 (PD1)
/Project Architecture/MCU - Unit/nFault17: IC2701.4 (nFAULT), LED2701.1 (K), R2703.2, TP2701.1, U401.33 (PD0)
/Project Architecture/MCU - Unit/nSLEEP_FRONT: IC1001.11 (nSLEEP), IC1101.11 (nSLEEP), IC1201.11 (nSLEEP), IC1301.11 (nSLEEP), IC1401.11 (nSLEEP), IC1501.11 (nSLEEP), IC1601.11 (nSLEEP), IC1701.11 (nSLEEP), IC1801.11 (nSLEEP), IC1901.11 (nSLEEP), IC2001.11 (nSLEEP), TP901.1
/Project Architecture/MCU - Unit/nSLEEP_REAR: IC2101.11 (nSLEEP), IC2201.11 (nSLEEP), IC2301.11 (nSLEEP), IC2401.11 (nSLEEP), IC2501.11 (nSLEEP), IC2601.11 (nSLEEP), IC2701.11 (nSLEEP), TP902.1
/Project Architecture/MCU - Unit/~RESET: C402.1, J402.3 (~RESET), SW402.2, SW402.3, U401.10 (NRST)
/Project Architecture/Misc - Mounting Holes & Fiducials/HOLE1: C2901.1, H2901.1, R2901.1
/Project Architecture/Misc - Mounting Holes & Fiducials/HOLE2: C2902.1, H2902.1, R2902.1
/Project Architecture/Misc - Mounting Holes & Fiducials/HOLE3: C2903.1, H2903.1, R2903.1
/Project Architecture/Misc - Mounting Holes & Fiducials/HOLE4: C2904.1, H2904.1, R2904.1
/Project Architecture/Motor Control - Drivers/Motor Control - Driver 0/FAULT_LED: LED1001.2 (A), R1002.2
/Project Architecture/Motor Control - Drivers/Motor Control - Driver 0/RC_OUT: IC1001.3 (RC_OUT), TP1002.1
/Project Architecture/Motor Control - Drivers/Motor Control - Driver 1/A0: IC1101.10 (A0), TP1105.1
/Project Architecture/Motor Control - Drivers/Motor Control - Driver 1/FAULT_LED: LED1101.2 (A), R1102.2
/Project Architecture/Motor Control - Drivers/Motor Control - Driver 1/RC_OUT: IC1101.3 (RC_OUT), TP1102.1
/Project Architecture/Motor Control - Drivers/Motor Control - Driver 2/FAULT_LED: LED1201.2 (A), R1202.2
/Project Architecture/Motor Control - Drivers/Motor Control - Driver 2/RC_OUT: IC1201.3 (RC_OUT), TP1202.1
/Project Architecture/Motor Control - Drivers/Motor Control - Driver 3/A1: IC1301.9 (A1), TP1306.1
/Project Architecture/Motor Control - Drivers/Motor Control - Driver 3/FAULT_LED: LED1301.2 (A), R1302.2
/Project Architecture/Motor Control - Drivers/Motor Control - Driver 3/RC_OUT: IC1301.3 (RC_OUT), TP1302.1
/Project Architecture/Motor Control - Drivers/Motor Control - Driver 4/A0: IC1401.10 (A0), TP1405.1
/Project Architecture/Motor Control - Drivers/Motor Control - Driver 4/A1: IC1401.9 (A1), TP1406.1
/Project Architecture/Motor Control - Drivers/Motor Control - Driver 4/FAULT_LED: LED1401.2 (A), R1402.2
/Project Architecture/Motor Control - Drivers/Motor Control - Driver 4/RC_OUT: IC1401.3 (RC_OUT), TP1402.1
/Project Architecture/Motor Control - Drivers/Motor Control - Driver 5/A1: IC1501.9 (A1), TP1506.1
/Project Architecture/Motor Control - Drivers/Motor Control - Driver 5/FAULT_LED: LED1501.2 (A), R1502.2
/Project Architecture/Motor Control - Drivers/Motor Control - Driver 5/RC_OUT: IC1501.3 (RC_OUT), TP1502.1
/Project Architecture/Motor Control - Drivers/Motor Control - Driver 6/FAULT_LED: LED1601.2 (A), R1602.2
/Project Architecture/Motor Control - Drivers/Motor Control - Driver 6/RC_OUT: IC1601.3 (RC_OUT), TP1602.1
/Project Architecture/Motor Control - Drivers/Motor Control - Driver 7/A0: IC1701.10 (A0), TP1705.1
/Project Architecture/Motor Control - Drivers/Motor Control - Driver 7/FAULT_LED: LED1701.2 (A), R1702.2
/Project Architecture/Motor Control - Drivers/Motor Control - Driver 7/RC_OUT: IC1701.3 (RC_OUT), TP1702.1
/Project Architecture/Motor Control - Drivers/Motor Control - Driver 8/FAULT_LED: LED1801.2 (A), R1802.2
/Project Architecture/Motor Control - Drivers/Motor Control - Driver 8/RC_OUT: IC1801.3 (RC_OUT), TP1802.1
/Project Architecture/Motor Control - Drivers/Motor Control - Driver 9/FAULT_LED: LED1901.2 (A), R1902.2
/Project Architecture/Motor Control - Drivers/Motor Control - Driver 9/RC_OUT: IC1901.3 (RC_OUT), TP1902.1
/Project Architecture/Motor Control - Drivers/Motor Control - Driver 10/A0: IC2001.10 (A0), TP2005.1
/Project Architecture/Motor Control - Drivers/Motor Control - Driver 10/FAULT_L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: LED2001.2 (A), R2002.2
/Project Architecture/Motor Control - Drivers/Motor Control - Driver 10/RC_OUT: IC2001.3 (RC_OUT), TP2002.1
/Project Architecture/Motor Control - Drivers/Motor Control - Driver 11/FAULT_L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: LED2101.2 (A), R2102.2
/Project Architecture/Motor Control - Drivers/Motor Control - Driver 11/RC_OUT: IC2101.3 (RC_OUT), TP2102.1
/Project Architecture/Motor Control - Drivers/Motor Control - Driver 12/A1: IC2201.9 (A1), TP2206.1
/Project Architecture/Motor Control - Drivers/Motor Control - Driver 12/FAULT_L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: LED2201.2 (A), R2202.2
/Project Architecture/Motor Control - Drivers/Motor Control - Driver 12/RC_OUT: IC2201.3 (RC_OUT), TP2202.1
/Project Architecture/Motor Control - Drivers/Motor Control - Driver 13/A0: IC2301.10 (A0), TP2305.1
/Project Architecture/Motor Control - Drivers/Motor Control - Driver 13/A1: IC2301.9 (A1), TP2306.1
/Project Architecture/Motor Control - Drivers/Motor Control - Driver 13/FAULT_L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: LED2301.2 (A), R2302.2
/Project Architecture/Motor Control - Drivers/Motor Control - Driver 13/RC_OUT: IC2301.3 (RC_OUT), TP2302.1
/Project Architecture/Motor Control - Drivers/Motor Control - Driver 14/A1: IC2401.9 (A1), TP2406.1
/Project Architecture/Motor Control - Drivers/Motor Control - Driver 14/FAULT_L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: LED2401.2 (A), R2402.2
/Project Architecture/Motor Control - Drivers/Motor Control - Driver 14/RC_OUT: IC2401.3 (RC_OUT), TP2402.1
/Project Architecture/Motor Control - Drivers/Motor Control - Driver 15/FAULT_L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: LED2501.2 (A), R2502.2
/Project Architecture/Motor Control - Drivers/Motor Control - Driver 15/RC_OUT: IC2501.3 (RC_OUT), TP2502.1
/Project Architecture/Motor Control - Drivers/Motor Control - Driver 16/A0: IC2601.10 (A0), TP2605.1
/Project Architecture/Motor Control - Drivers/Motor Control - Driver 16/FAULT_L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: LED2601.2 (A), R2602.2
/Project Architecture/Motor Control - Drivers/Motor Control - Driver 16/RC_OUT: IC2601.3 (RC_OUT), TP2602.1
/Project Architecture/Motor Control - Drivers/Motor Control - Driver 17/FAULT_L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: LED2701.2 (A), R2702.2
/Project Architecture/Motor Control - Drivers/Motor Control - Driver 17/RC_OUT: IC2701.3 (RC_OUT), TP2702.1
/Project Architecture/Motor Control - Drivers/OUT1_0: IC1001.6 (OUT1), J901.2, TP1003.1
/Project Architecture/Motor Control - Drivers/OUT1_1: IC1101.6 (OUT1), J901.4, TP1103.1
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

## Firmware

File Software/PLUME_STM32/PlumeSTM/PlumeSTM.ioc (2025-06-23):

#MicroXplorer Configuration settings - do not modify
ADC1.Channel-1\#ChannelRegularConversion=ADC_CHANNEL_6
ADC1.CommonPathInternal=null|null|null|null
ADC1.IPParameters=Rank-1\#ChannelRegularConversion,Channel-1\#ChannelRegularConversion,SamplingTime-1\#ChannelRegularConversion,OffsetNumber-1\#ChannelRegularConversion,NbrOfConversionFlag,master,CommonPathInternal
ADC1.NbrOfConversionFlag=1
ADC1.OffsetNumber-1\#ChannelRegularConversion=ADC_OFFSET_NONE
ADC1.Rank-1\#ChannelRegularConversion=1
ADC1.SamplingTime-1\#ChannelRegularConversion=ADC_SAMPLETIME_47CYCLES_5
ADC1.master=1
CAD.formats=
CAD.pinconfig=
CAD.provider=
Dma.Request0=SPI2_TX
Dma.Request1=USART1_RX
Dma.Request2=USART1_TX
Dma.RequestsNb=3
Dma.SPI2_TX.0.Direction=DMA_MEMORY_TO_PERIPH
Dma.SPI2_TX.0.EventEnable=DISABLE
Dma.SPI2_TX.0.Instance=DMA1_Channel1
Dma.SPI2_TX.0.MemDataAlignment=DMA_MDATAALIGN_BYTE
Dma.SPI2_TX.0.MemInc=DMA_MINC_ENABLE
Dma.SPI2_TX.0.Mode=DMA_NORMAL
Dma.SPI2_TX.0.PeriphDataAlignment=DMA_PDATAALIGN_BYTE
Dma.SPI2_TX.0.PeriphInc=DMA_PINC_DISABLE
Dma.SPI2_TX.0.Polarity=HAL_DMAMUX_REQ_GEN_RISING
Dma.SPI2_TX.0.Priority=DMA_PRIORITY_LOW
Dma.SPI2_TX.0.RequestNumber=1
Dma.SPI2_TX.0.RequestParameters=Instance,Direction,PeriphInc,MemInc,PeriphDataAlignment,MemDataAlignment,Mode,Priority,SignalID,Polarity,RequestNumber,SyncSignalID,SyncPolarity,SyncEnable,EventEnable,SyncRequestNumber
Dma.SPI2_TX.0.SignalID=NONE
Dma.SPI2_TX.0.SyncEnable=DISABLE
Dma.SPI2_TX.0.SyncPolarity=HAL_DMAMUX_SYNC_NO_EVENT
Dma.SPI2_TX.0.SyncRequestNumber=1
Dma.SPI2_TX.0.SyncSignalID=NONE
Dma.USART1_RX.1.Direction=DMA_PERIPH_TO_MEMORY
Dma.USART1_RX.1.EventEnable=DISABLE
Dma.USART1_RX.1.Instance=DMA1_Channel2
Dma.USART1_RX.1.MemDataAlignment=DMA_MDATAALIGN_BYTE
Dma.USART1_RX.1.MemInc=DMA_MINC_ENABLE
Dma.USART1_RX.1.Mode=DMA_CIRCULAR
Dma.USART1_RX.1.PeriphDataAlignment=DMA_PDATAALIGN_BYTE
Dma.USART1_RX.1.PeriphInc=DMA_PINC_DISABLE
Dma.USART1_RX.1.Polarity=HAL_DMAMUX_REQ_GEN_RISING
Dma.USART1_RX.1.Priority=DMA_PRIORITY_LOW
Dma.USART1_RX.1.RequestNumber=1
Dma.USART1_RX.1.RequestParameters=Instance,Direction,PeriphInc,MemInc,PeriphDataAlignment,MemDataAlignment,Mode,Priority,SignalID,Polarity,RequestNumber,SyncSignalID,SyncPolarity,SyncEnable,EventEnable,SyncRequestNumber
Dma.USART1_RX.1.SignalID=NONE
Dma.USART1_RX.1.SyncEnable=DISABLE
Dma.USART1_RX.1.SyncPolarity=HAL_DMAMUX_SYNC_NO_EVENT
Dma.USART1_RX.1.SyncRequestNumber=1
Dma.USART1_RX.1.SyncSignalID=NONE
Dma.USART1_TX.2.Direction=DMA_MEMORY_TO_PERIPH
Dma.USART1_TX.2.EventEnable=DISABLE
Dma.USART1_TX.2.Instance=DMA1_Channel3
Dma.USART1_TX.2.MemDataAlignment=DMA_MDATAALIGN_BYTE
Dma.USART1_TX.2.MemInc=DMA_MINC_ENABLE
Dma.USART1_TX.2.Mode=DMA_NORMAL
Dma.USART1_TX.2.PeriphDataAlignment=DMA_PDATAALIGN_BYTE
Dma.USART1_TX.2.PeriphInc=DMA_PINC_DISABLE
Dma.USART1_TX.2.Polarity=HAL_DMAMUX_REQ_GEN_RISING
Dma.USART1_TX.2.Priority=DMA_PRIORITY_LOW
Dma.USART1_TX.2.RequestNumber=1
Dma.USART1_TX.2.RequestParameters=Instance,Direction,PeriphInc,MemInc,PeriphDataAlignment,MemDataAlignment,Mode,Priority,SignalID,Polarity,RequestNumber,SyncSignalID,SyncPolarity,SyncEnable,EventEnable,SyncRequestNumber
Dma.USART1_TX.2.SignalID=NONE
Dma.USART1_TX.2.SyncEnable=DISABLE
Dma.USART1_TX.2.SyncPolarity=HAL_DMAMUX_SYNC_NO_EVENT
Dma.USART1_TX.2.SyncRequestNumber=1
Dma.USART1_TX.2.SyncSignalID=NONE
File.Version=6
GPIO.groupedBy=Group By Peripherals
I2C1.I2C_Speed_Mode=I2C_Fast
I2C1.IPParameters=Timing,I2C_Speed_Mode
I2C1.Timing=0x0070133F
I2C3.I2C_Speed_Mode=I2C_Fast
I2C3.IPParameters=Timing,I2C_Speed_Mode
I2C3.Timing=0x0070133F
KeepUserPlacement=false
MMTAppRegionsCount=0
MMTConfigApplied=false
Mcu.CPN=STM32WB5MMGH6TR
Mcu.Family=STM32WB
Mcu.IP0=ADC1
Mcu.IP1=DMA
Mcu.IP10=SPI2
Mcu.IP11=SYS
Mcu.IP12=TIM2
Mcu.IP13=TIM16
Mcu.IP14=USART1
Mcu.IP2=HSEM
Mcu.IP3=I2C1
Mcu.IP4=I2C3
Mcu.IP5=IPCC
Mcu.IP6=MEMORYMAP
Mcu.IP7=NVIC
Mcu.IP8=RCC
Mcu.IP9=RTC
Mcu.IPNb=15
Mcu.Name=STM32WB5MMGHx
Mcu.Package=LGA86
Mcu.Pin0=PA2
Mcu.Pin1=PA1
Mcu.Pin10=PB7
Mcu.Pin11=PB5
Mcu.Pin12=PB4
Mcu.Pin13=PB3
Mcu.Pin14=PC10
Mcu.Pin15=PA13
Mcu.Pin16=PA14
Mcu.Pin17=PA15
Mcu.Pin18=PA10
Mcu.Pin19=PD0
Mcu.Pin2=PA0
Mcu.Pin20=PD1
Mcu.Pin21=PB13
Mcu.Pin22=PB12
Mcu.Pin23=PE4
Mcu.Pin24=PB10
Mcu.Pin25=PC4
Mcu.Pin26=PA8
Mcu.Pin27=PA9
Mcu.Pin28=PA7
Mcu.Pin29=PA6
Mcu.Pin3=PC3
Mcu.Pin30=PA5
Mcu.Pin31=PA3
Mcu.Pin32=PH0
Mcu.Pin33=PH1
Mcu.Pin34=PD14
Mcu.Pin35=PE1
Mcu.Pin36=PD13
Mcu.Pin37=PD12
Mcu.Pin38=PD3
Mcu.Pin39=PC7
Mcu.Pin4=PC2
Mcu.Pin40=PE3
Mcu.Pin41=PD4
Mcu.Pin42=PD15
Mcu.Pin43=PD10
Mcu.Pin44=PE2
Mcu.Pin45=PE0
Mcu.Pin46=VP_HSEM_VS_HSEM
Mcu.Pin47=VP_IPCC_VS_IPCC
Mcu.Pin48=VP_RCC_V_OSC_IN
Mcu.Pin49=VP_RCC_V_OSC32_IN
Mcu.Pin5=PC1
Mcu.Pin50=VP_RTC_VS_RTC_Activate
Mcu.Pin51=VP_RTC_VS_RTC_WakeUp_intern
Mcu.Pin52=VP_SYS_V_PVD_IN
Mcu.Pin53=VP_SYS_VS_Systick
Mcu.Pin54=VP_TIM2_VS_ClockSourceINT
Mcu.Pin55=VP_TIM16_VS_ClockSourceINT
Mcu.Pin56=VP_MEMORYMAP_VS_MEMORYMAP
Mcu.Pin6=PB9
Mcu.Pin7=PC0
Mcu.Pin8=PH3-BOOT0
Mcu.Pin9=PB8
Mcu.PinsNb=57
Mcu.ThirdPartyNb=0
Mcu.UserConstants=
Mcu.UserName=STM32WB5MMGHx
MxCube.Version=6.14.1
MxDb.Version=DB.6.0.141
NVIC.BusFault_IRQn=true\:0\:0\:false\:false\:true\:false\:false\:false
NVIC.DMA1_Channel1_IRQn=true\:0\:0\:false\:false\:true\:false\:true\:true
NVIC.DMA1_Channel2_IRQn=true\:0\:0\:false\:false\:true\:false\:true\:true
NVIC.DMA1_Channel3_IRQn=true\:0\:0\:false\:false\:true\:false\:true\:true
NVIC.DebugMonitor_IRQn=true\:0\:0\:false\:false\:true\:false\:false\:false
NVIC.EXTI0_IRQn=true\:0\:0\:false\:false\:true\:true\:true\:true
NVIC.EXTI15_10_IRQn=true\:0\:0\:false\:false\:true\:true\:true\:true
NVIC.EXTI3_IRQn=true\:0\:0\:false\:false\:true\:true\:true\:true
NVIC.EXTI4_IRQn=true\:0\:0\:false\:false\:true\:true\:true\:true
NVIC.EXTI9_5_IRQn=true\:0\:0\:false\:false\:true\:true\:true\:true
NVIC.ForceEnableDMAVector=true
NVIC.HSEM_IRQn=true\:0\:0\:false\:false\:true\:false\:true\:true
NVIC.HardFault_IRQn=true\:0\:0\:false\:false\:true\:false\:false\:false
NVIC.IPCC_C1_RX_IRQn=true\:0\:0\:false\:false\:true\:true\:true\:true
NVIC.IPCC_C1_TX_IRQn=true\:0\:0\:false\:false\:true\:true\:true\:true
NVIC.MemoryManagement_IRQn=true\:0\:0\:false\:false\:true\:false\:false\:false
NVIC.NonMaskableInt_IRQn=true\:0\:0\:false\:false\:true\:false\:false\:false
NVIC.PendSV_IRQn=true\:0\:0\:false\:false\:true\:false\:false\:false
NVIC.PriorityGroup=NVIC_PRIORITYGROUP_4
NVIC.RTC_WKUP_IRQn=true\:0\:0\:false\:false\:true\:true\:true\:true
NVIC.SPI2_IRQn=true\:0\:0\:false\:false\:true\:true\:true\:true
NVIC.SVCall_IRQn=true\:0\:0\:false\:false\:true\:false\:false\:false
NVIC.SysTick_IRQn=true\:15\:0\:false\:false\:true\:false\:true\:false
NVIC.TIM1_UP_TIM16_IRQn=true\:0\:0\:false\:false\:true\:true\:true\:true
NVIC.TIM2_IRQn=true\:0\:0\:false\:false\:true\:true\:true\:true
NVIC.USART1_IRQn=true\:0\:0\:false\:false\:true\:true\:true\:true
NVIC.UsageFault_IRQn=true\:0\:0\:false\:false\:true\:false\:false\:false
PA0.GPIOParameters=GPIO_PuPd,GPIO_Label
PA0.GPIO_Label=IMU_INT1
PA0.GPIO_PuPd=GPIO_PULLDOWN
PA0.Locked=true
PA0.Signal=GPXTI0
PA1.GPIOParameters=GPIO_Label
PA1.GPIO_Label=BAT_SENSE
PA1.Locked=true
PA1.Signal=ADCx_IN6
PA10.GPIOParameters=GPIO_Speed
PA10.GPIO_Speed=GPIO_SPEED_FREQ_HIGH
PA10.Locked=true
PA10.Mode=Asynchronous
PA10.Signal=USART1_RX
PA13.Locked=true
PA13.Mode=Trace_Asynchronous_SW
PA13.Signal=SYS_JTMS-SWDIO
PA14.Mode=Trace_Asynchronous_SW
PA14.Signal=SYS_JTCK-SWCLK
PA15.GPIOParameters=PinState,GPIO_Label
PA15.GPIO_Label=MUX_RESET
PA15.Locked=true
PA15.PinState=GPIO_PIN_SET
PA15.Signal=GPIO_Output
PA2.GPIOParameters=GPIO_Label
PA2.GPIO_Label=EN2
PA2.Locked=true
PA2.Signal=GPIO_Output
PA3.GPIOParameters=GPIO_Label
PA3.GPIO_Label=EN1
PA3.Locked=true
PA3.Signal=GPIO_Output
PA5.GPIOParameters=GPIO_PuPd,GPIO_Label
PA5.GPIO_Label=nFAULT10
PA5.GPIO_PuPd=GPIO_PULLUP
PA5.Locked=true
PA5.Signal=GPIO_Input
PA6.GPIOParameters=GPIO_PuPd,GPIO_Label
PA6.GPIO_Label=nFAULT0
PA6.GPIO_PuPd=GPIO_PULLUP
PA6.Locked=true
PA6.Signal=GPIO_Input
PA7.GPIOParameters=GPIO_PuPd,GPIO_Label
PA7.GPIO_Label=nFAULT16
PA7.GPIO_PuPd=GPIO_PULLUP
PA7.Locked=true
PA7.Signal=GPIO_Input
PA8.GPIOParameters=GPIO_PuPd,GPIO_Label
PA8.GPIO_Label=nFAULT11
PA8.GPIO_PuPd=GPIO_PULLUP
PA8.Locked=true
PA8.Signal=GPIO_Input
PA9.GPIOParameters=GPIO_Speed
PA9.GPIO_Speed=GPIO_SPEED_FREQ_HIGH
PA9.Locked=true
PA9.Mode=Asynchronous
PA9.Signal=USART1_TX
PB10.Mode=TX_Only_Simplex_Unidirect_Master
PB10.Signal=SPI2_SCK
PB12.GPIOParameters=GPIO_PuPd,GPIO_Label
PB12.GPIO_Label=nFAULT8
PB12.GPIO_PuPd=GPIO_PULLUP
PB12.Locked=true
PB12.Signal=GPIO_Input
PB13.GPIOParameters=GPIO_PuPd,GPIO_Label
PB13.GPIO_Label=nFAULT15
PB13.GPIO_PuPd=GPIO_PULLUP
PB13.Locked=true
PB13.Signal=GPIO_Input
PB3.Locked=true
PB3.Mode=Trace_Asynchronous_SW
PB3.Signal=SYS_JTDO-SWO
PB4.GPIOParameters=GPIO_PuPd,GPIO_Label,GPIO_ModeDefaultEXTI
PB4.GPIO_Label=BUTTON3
PB4.GPIO_ModeDefaultEXTI=GPIO_MODE_IT_FALLING
PB4.GPIO_PuPd=GPIO_PULLUP
PB4.Locked=true
PB4.Signal=GPXTI4
PB5.GPIOParameters=GPIO_PuPd,GPIO_Label,GPIO_ModeDefaultEXTI
PB5.GPIO_Label=BUTTON2
PB5.GPIO_ModeDefaultEXTI=GPIO_MODE_IT_FALLING
PB5.GPIO_PuPd=GPIO_PULLUP
PB5.Locked=true
PB5.Signal=GPXTI5
PB7.GPIOParameters=GPIO_PuPd,GPIO_Label,GPIO_ModeDefaultEXTI
PB7.GPIO_Label=BUTTON1
PB7.GPIO_ModeDefaultEXTI=GPIO_MODE_IT_FALLING
PB7.GPIO_PuPd=GPIO_PULLUP
PB7.Locked=true
PB7.Signal=GPXTI7
PB8.Mode=I2C
PB8.Signal=I2C1_SCL
PB9.Mode=I2C
PB9.Signal=I2C1_SDA
PC0.Locked=true
PC0.Mode=I2C
PC0.Signal=I2C3_SCL
PC1.Locked=true
PC1.Mode=I2C
PC1.Signal=I2C3_SDA
PC10.GPIOParameters=GPIO_PuPd,GPIO_Label,GPIO_ModeDefaultEXTI
PC10.GPIO_Label=BUTTON4
PC10.GPIO_ModeDefaultEXTI=GPIO_MODE_IT_FALLING
PC10.GPIO_PuPd=GPIO_PULLUP
PC10.Locked=true
PC10.Signal=GPXTI10
PC2.GPIOParameters=GPIO_Speed,GPIO_Label
PC2.GPIO_Label=LED_5V_EN
PC2.GPIO_Speed=GPIO_SPEED_FREQ_HIGH
PC2.Locked=true
PC2.Signal=GPIO_Output
PC3.GPIOParameters=GPIO_Speed
PC3.GPIO_Speed=GPIO_SPEED_FREQ_VERY_HIGH
PC3.Locked=true
PC3.Mode=TX_Only_Simplex_Unidirect_Master
PC3.Signal=SPI2_MOSI
PC4.GPIOParameters=GPIO_PuPd,GPIO_Label
PC4.GPIO_Label=nFAULT12
PC4.GPIO_PuPd=GPIO_PULLUP
PC4.Locked=true
PC4.Signal=GPIO_Input
PC7.GPIOParameters=GPIO_Label
PC7.GPIO_Label=nSLEEP_REAR
PC7.Locked=true
PC7.Signal=GPIO_Output
PCC.Ble.ConnectionInterval=1000.0
PCC.Ble.DataLength=6
PCC.Ble.IsUsed=false
PCC.Ble.Mode=NOT_SELECTED
PCC.Ble.PowerLevel=Min
PCC.Zigbee.IsUsed=false
PCC.Zigbee.Mode=Sleepy End Device
PCC.Zigbee.Payload=15
PCC.Zigbee.PoolPeriodicity=480.0
PCC.Zigbee.PowerLevel=Min
PCC.Zigbee.RequestPeriodicity=1500.0
PD0.GPIOParameters=GPIO_PuPd,GPIO_Label
PD0.GPIO_Label=nFAULT13
PD0.GPIO_PuPd=GPIO_PULLUP
PD0.Locked=true
PD0.Signal=GPIO_Input
PD1.GPIOParameters=GPIO_PuPd,GPIO_Label
PD1.GPIO_Label=nFAULT17
PD1.GPIO_PuPd=GPIO_PULLUP
PD1.Locked=true
PD1.Signal=GPIO_Input
PD10.GPIOParameters=GPIO_PuPd,GPIO_Label
PD10.GPIO_Label=nFAULT1
PD10.GPIO_PuPd=GPIO_PULLUP
PD10.Locked=true
PD10.Signal=GPIO_Input
PD12.GPIOParameters=GPIO_Label
PD12.GPIO_Label=IMU_INT2
PD12.Locked=true
PD12.Signal=GPIO_Input
PD13.GPIOParameters=GPIO_PuPd,GPIO_Label
PD13.GPIO_Label=nFAULT4
PD13.GPIO_PuPd=GPIO_PULLUP
PD13.Locked=true
PD13.Signal=GPIO_Input
PD14.GPIOParameters=GPIO_PuPd,GPIO_Label
PD14.GPIO_Label=nFAULT3
PD14.GPIO_PuPd=GPIO_PULLUP
PD14.Locked=true
PD14.Signal=GPIO_Input
PD15.GPIOParameters=GPIO_Label
PD15.GPIO_Label=CHARGE_STATUS
PD15.Locked=true
PD15.Signal=GPIO_Input
PD3.GPIOParameters=GPIO_PuPd,GPIO_Label
PD3.GPIO_Label=nFAULT14
PD3.GPIO_PuPd=GPIO_PULLUP
PD3.Locked=true
PD3.Signal=GPIO_Input
PD4.GPIOParameters=GPIO_Label
PD4.GPIO_Label=SWITCH2
PD4.Locked=true
PD4.Signal=GPIO_Input
PE0.GPIOParameters=GPIO_PuPd,GPIO_Label
PE0.GPIO_Label=nFAULT6
PE0.GPIO_PuPd=GPIO_PULLUP
PE0.Locked=true
PE0.Signal=GPIO_Input
PE1.GPIOParameters=GPIO_Label
PE1.GPIO_Label=nSLEEP_FRONT
PE1.Locked=true
PE1.Signal=GPIO_Output
PE2.GPIOParameters=GPIO_PuPd,GPIO_Label
PE2.GPIO_Label=nFAULT7
PE2.GPIO_PuPd=GPIO_PULLUP
PE2.Locked=true
PE2.Signal=GPIO_Input
PE3.GPIOParameters=GPIO_Label
PE3.GPIO_Label=SWITCH1
PE3.Locked=true
PE3.Signal=GPIO_Input
PE4.GPIOParameters=GPIO_PuPd,GPIO_Label
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

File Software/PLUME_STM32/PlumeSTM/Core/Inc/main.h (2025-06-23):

/* USER CODE BEGIN Header */
/**
  ******************************************************************************
  * @file           : main.h
  * @brief          : Header for main.c file.
  *                   This file contains the common defines of the application.
  ******************************************************************************
  * @attention
  *
  * Copyright (c) 2025 STMicroelectronics.
  * All rights reserved.
  *
  * This software is licensed under terms that can be found in the LICENSE file
  * in the root directory of this software component.
  * If no LICENSE file comes with this software, it is provided AS-IS.
  *
  ******************************************************************************
  */
/* USER CODE END Header */

/* Define to prevent recursive inclusion -------------------------------------*/
#ifndef __MAIN_H
#define __MAIN_H

#ifdef __cplusplus
extern "C" {
#endif

/* Includes ------------------------------------------------------------------*/
#include "stm32wbxx_hal.h"

/* Private includes ----------------------------------------------------------*/
/* USER CODE BEGIN Includes */

/* USER CODE END Includes */

/* Exported types ------------------------------------------------------------*/
/* USER CODE BEGIN ET */

/* USER CODE END ET */

/* Exported constants --------------------------------------------------------*/
/* USER CODE BEGIN EC */

/* USER CODE END EC */

/* Exported macro ------------------------------------------------------------*/
/* USER CODE BEGIN EM */

/* USER CODE END EM */

/* Exported functions prototypes ---------------------------------------------*/
void Error_Handler(void);

/* USER CODE BEGIN EFP */
void SystemClock_Config(void);
/* USER CODE END EFP */
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

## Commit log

2025-02-28 Project code main.cpp updated
    [Motor resistance.xlsx]
2025-03-28 Finished 65% of schematics
    [Block Diagram.kicad_sch, Logic_I2C_Mux.kicad_sch, MCU_Unit.kicad_sch, Misc - Mounting Holes.kicad_sch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]
2025-03-31 Added footprints, images, almost finished all èages except for the MCU
    [Block Diagram.kicad_sch, Logic_I2C_Mux.kicad_sch, MCU_Unit.kicad_sch, Misc - Mounting Holes.kicad_sch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]
2025-04-01 Added RGB LED, added motor connectors, added test points, imported all 3D models
    [Logic_I2C_Mux.kicad_sch, MCU_Unit.kicad_sch, Misc_Mounting_Holes.kicad_sch, Motor_Control_Driver.kicad_sch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]
2025-04-04 Finished schematic, imported all footprints, all 3D models and created STM32 project, now need to proofread shematic before layout
    [Logic_I2C_Mux.kicad_sch, MCU_Unit.kicad_sch, Misc_Mounting_Holes.kicad_sch, Motor_Control_Driver.kicad_sch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]
2025-04-05 Reviewed shematic, cleaned all DRC errors, chosed stackup, started layout
    [Block Diagram.kicad_sch, Logic_I2C_Mux.kicad_sch, MCU_Unit.kicad_sch, Misc_Mounting_Holes.kicad_sch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]
2025-04-05 Cleaned repo, cleaned and exported shematic, advanced rough layout
    [Block Diagram.kicad_sch, Logic_I2C_Mux.kicad_sch, MCU_Unit.kicad_sch, Misc_Mounting_Holes.kicad_sch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]
2025-04-13 Advanced rough layout
    [Logic_I2C_Mux.kicad_sch, MCU_Unit.kicad_sch, Motor_Control_Driver.kicad_sch, Motor_Control_Drivers.kicad_sch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]
2025-04-14 Finished layout, only cleaning left
    [Logic_I2C_Mux.kicad_sch, MCU_Unit.kicad_sch, Misc_Mounting_Holes.kicad_sch, Motor_Control_Driver.kicad_sch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]
2025-04-14 Finished cleaning routing, removed errors, cleaned shematics, added pictures and other improvements
    [Logic_I2C_Mux.kicad_sch, MCU_Unit.kicad_sch, Misc_Mounting_Holes.kicad_sch, Motor_Control_Driver.kicad_sch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]
2025-04-17 Added PCB frame
    [Logic_I2C_Mux.kicad_sch, MCU_Unit.kicad_sch, Misc_Mounting_Holes.kicad_sch, Motor_Control_Driver.kicad_sch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]
2025-04-19 Added PCB frame for assembly, almost finished auto-review, only MCU and motors left
    [Logic_I2C_Mux.kicad_sch, MCU_Unit.kicad_sch, Misc_Mounting_Holes.kicad_sch, Motor_Control_Driver.kicad_sch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]
2025-04-21 Checked everything, corrected footprints, cleaned routing, should be ready to order
    [Logic_I2C_Mux.kicad_sch, MCU_Unit.kicad_sch, Motor_Control_Driver.kicad_sch, Motor_Control_Drivers.kicad_sch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]
2025-04-21 Checked MCU pinout, cleaned shematic, advanced the ioc file
    [Logic_I2C_Mux.kicad_sch, MCU_Unit.kicad_sch, Misc_Mounting_Holes.kicad_sch, Motor_Control_Driver.kicad_sch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]
2025-04-24 Final version, cleaned and ordered as is
    [Basket_Mouser.xlsx, Logic_I2C_Mux.kicad_sch, MCU_Unit.kicad_sch, Misc_Mounting_Holes.kicad_sch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]
2025-05-17 Started on the STM32 firmware
    [Logic_I2C_Mux.kicad_sch, MCU_Unit.kicad_sch, Motor_Control_Driver.kicad_sch, Motor_Control_Drivers.kicad_sch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]
2025-05-19 Working IMU, motors and all, next step, low power..
2025-05-26 Cleaned repo, remnamed folder, added latest version of drv8214 library
    [Logic_I2C_Mux.kicad_sch, MCU_Unit.kicad_sch, Motor_Control_Driver.kicad_sch, Motor_Control_Drivers.kicad_sch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]
2025-06-19 Push before migrating main to functions.h
    [Basket_Mouser.xlsx, Logic_I2C_Mux.kicad_sch, MCU_Unit.kicad_sch, Motor_Control_Driver.kicad_sch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]
